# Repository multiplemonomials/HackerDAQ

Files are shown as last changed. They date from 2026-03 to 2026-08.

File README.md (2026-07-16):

# HackerDAQ: A Data Acquisition System for Hackers

HackerDAQ is a work-in-progress project to create an open-source data acquisition system. The project is currently in its early stages, but the goal is to create something that can be used in place of industrial DAQ systems to record high-quality data.

## Background and Motivation

The tech industry is in kind of a weird place when it comes to data acquisition (DAQ) systems. Suppose you have some sort of mechanical system you want to work with -- maybe a science experiment, maybe an industrial process, maybe an automation system, who knows. You have some sensors that you need to read and record the data from, and maybe you want to control some outputs as well, like turning the power on to some valves/solenoids/motors in response to a sensor reading. To do this, you need a DAQ system. However, an odd divide exists in the DAQ industry right now, between the incredibly professional and the almost insultingly hobbyist.

At one end of the spectrum, there are industrial-grade offerings from companies like National Instruments, Beckhoff, and Dewesoft. These systems are capable, flexible, and reliable -- but also extremely expensive. Even an entry-level NI system will run you well into the mid 4 figures, and other manufacturers are similar or worse. What if you can't afford that? Well, in many cases, your only option is getting an Arduino or Raspberry Pi and some basic dev boards for the sensors you need, and then hacking together enough software to log the data over serial. I've seen this many times, and while it does sometimes work, by doing it, you give up a lot of niceties like defined accuracy, noise resistance, a constant sample rate, etc.

Meanwhile, technology has moved on, and we're now in an era where highly accurate, multi-input Analog-Digital Converter (ADC) chips can be purchased very cheaply. This project has selected the [AD7770](https://www.analog.com/en/products/ad7770.html) from Analog Devices, a 21-bit, 32kHz, 8-input ADC which can be purchased for about $15 each at quantity. Using this chip enables DAQ devices to be made quite simply and cheaply, as one basically just needs to attach different front-ends to this chip to convert the signals based on the sensor being sampled. With the existence of this chip and others like it, there is really no justification for DAQ devices to cost thousands of dollars unless you need better accuracy or sampling rate than these types of ADCs can provide.

## Basic Overview

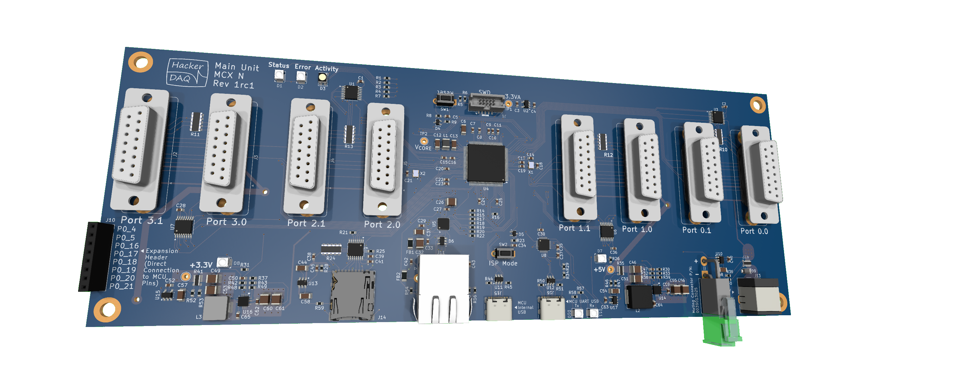
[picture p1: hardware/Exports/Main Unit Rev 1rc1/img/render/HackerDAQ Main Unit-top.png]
Main unit render


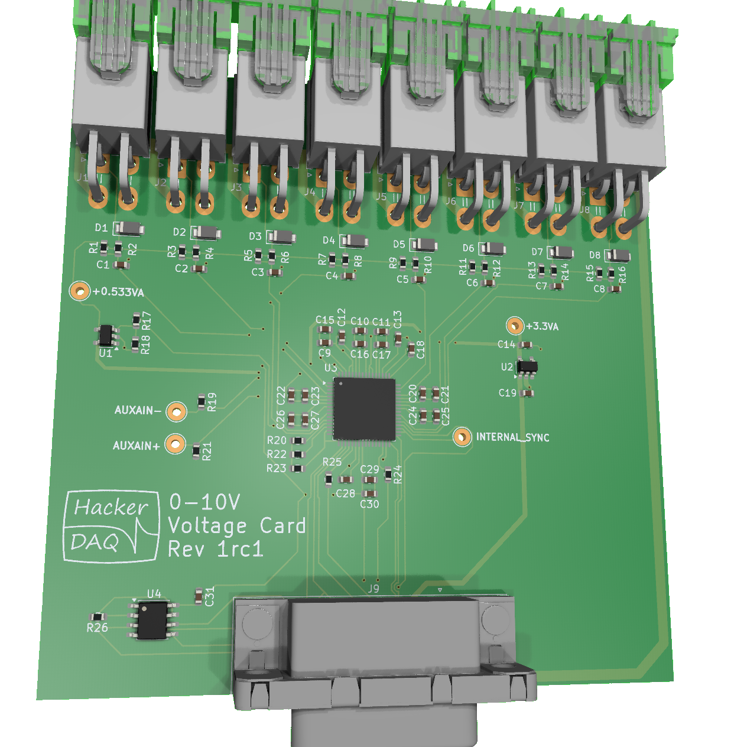
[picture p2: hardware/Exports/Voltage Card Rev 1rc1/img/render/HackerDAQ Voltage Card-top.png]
Voltage card render


The HackerDAQ consists of a main board with a microcontroller on it and basic circuitry such as power supplies, an Ethernet port, and a MicroSD slot. The main board would have a number of connectors for cards to plug in, each of which carries power, GPIOs, and SPI bus signals.

Cards can be designed for many different applications, including digital I/O and many different types of analog sensors. The user can select only the cards they need for the application they have in mind, keeping the base cost of the system down and allowing the user to get exactly the I/O they need. The SPI bus was selected for communications with these cards as it is fast, there are a wide range of chips available that speak it, and it supports bussing together multiple chips on the card over one set of bus lines. In a lot of ways, these cards are similar to existing sensor interconnect systems like SparkFun Qwiic / Adafruit Stemma / Digilent Pmod, where you can buy various task-specific modules and connect them to a motherboard. This would just be focused more on DAQ stuff and be more industrial-grade.

In terms of software, the HackerDAQ would include firmware that would run on the board and interface with all the cards, send data to connected user interface(s), and receive and execute commands. On the PC side, there would be a basic program that can display and record data. For users who don't want to program, they can see the live data in the GUI, record it to a file, and manually control outputs. For users who are a little more comfortable with programming, they could write scripts (likely python) that would run on the host machine and be able to control the DAQ. And for users who have embedded software experience, they could write their own code that extends or replaces the firmware on the actual DAQ!

## Key Decisions

| Area | Decision | Why |
|------------|-------------|--------------|
|Physical architecture | Main board + swappable cards | <ul><li>Avoids need to create multi-function inputs which would increase complexity</li><li>Makes system cheaper if you only need a few types of inputs</li><li>Avoids need to mess around with external amplifiers or other circuitry for sensors that need them -- they can be built directly into the card</li><li>Allows for much wider range of off-the-shelf supported functionality</li></ul>|
|CPU|NXP MCX Alpha Microcontroller running Mbed OS|<ul><li>Using a microcontroller, rather than a linux CPU + supporting circuitry, keeps the cost down</li><li>Using an RTOS rather than a full OS makes microsecond-level timestamping and SPI transaction scheduling possible</li><li>This MCU has two CPU cores at 150 MHz, plus a powerful DMA controller, a fast internal bus, and lots of SPI connectivity</li></ul>|
|SPI bus topology|2 card connectors per SPI bus, one leader card and one follower. All cards on a given bus must share the same polling rate.|<ul><li>MCU does not have enough pins for each of the 8 slots to have its own dedicated SPI bus, so there needs to be some way for cards to share a bus.</li><li>In most real systems, you generally have a lot of sensors at the same data rate, so I do not expect this to be too crippling of a limitation</li></ul>|
|Connection to host|Ethernet, potential upgrade later to add USB|<ul><li>Ethernet provides high quality electrical isolation and is highly noise-immune, so it's great for industrial applications</li><li>Ethernet peripherals in microcontrollers are well-optimized for high data rate applications</li><li>Allows the DAQ to connect to a larger network and interact with multiple machines, plus receive time via NTP</li></ul>|
|Local recording|MicroSD (SPI based)|<ul><li>Important to have a method of locally recording data for standalone applications</li><li>Mbed has a preexisting driver for MicroSD cards in SPI mode</li><li>SDIO mode is faster but driver support is less present (though not totally hopeless either)</li></ul>|
|Card identification|4kiB SPI EEPROM on the card (thinking M95320-RMN6)|<ul><li>Allows SW to largely autoconfigure itself based on the cards that are physically installed</li><li>Provides a convenient place to store calibration data!</li></ul>|
|Card to sensor connectors|Molex Mini-Fit|<ul><li>I have used these connectors in the past and they are really balanced all-around:<ul><li>Retention clip ensures they can't vibrate loose</li><li>Rated for ~8A continuous per pin</li><li>Good size: not so small that they are hard to work with, but not so big that they make your entire system bigger</li></ul></li><li>Big downside is that the crimp tool costs $400. Could mitigate by supplying one wire harness with each card that users can splice their own sensor wires to</li></ul>|
|Card to main board connector|15-pin, 2 row D-Sub (DA-15)|<ul><li>Very cheap</li><li>Screws provide relatively beefy mechanical retention</li><li>Not a size used in consumer hardware so unlikely to be plugged in to, say, a monitor accidentally</li><li>Still uses standard D-sub hardware so it should be possible to get premade cables, crimpers, etc without too much trouble</li></ul>|

## The Main Unit
The main unit contains a high performance MCX Alpha microcontroller with Ethernet, multiple SPI busses, a MicroSD slot, and a number of extra GPIO pins. 

### Data Recording
Both the Ethernet and the MicroSD card are available for recording data. The Ethernet is for livestreaming when you want to view, record, and process data on a PC, while the MicroSD card would be used for simple applications where you just want to record locally, and could also be configured as a backup so that data isn’t lost if the ethernet connection drops out.

### Power
The main unit takes in and regulates power for the HackerDAQ system. It has a DC input which can handle up to 8A at a variable voltage (9-24V). This voltage, referred to as Vsupply, is sent through the connectors into the cards for use as a higher voltage excitation supply when needed. High-current logic rails are provided for cards and attached devices to use -- currently 5V@8A and 3.3V@8A.

### Card Ports
The main unit has four SPI busses. Each SPI bus provides two card ports, a "leader" port and a "follower" port. The leader and follower ports on a given bus can have different cards connected, but *must* operate at the same speed as SPI transactions for all cards will happen at a fixed cycle rate for the bus.

### Expansion Port
Some of the microcontroller I/O pins that are not connected to one of the SPI busses are routed to the expansion port. This will include some digital pins (with I2C/PWM/UART) and some analog pins. Advanced users who are comfortable programming embedded C++ can add write their own software that uses these pins. This allows the HackerDAQ to be used as a jumping-off point for one's own projects!

Also, SWD debug pins and reset pin are broken out to an ARM SWD debug connector, for use with a debug tool like a J-Link or MCU-Link.

### Open Questions
- Is it worth adding a battery-backed RTC so that the time can be maintained if there is a power outage?
- Does PoE support make sense?

### Card Interface
The main unit would provide the following signals to each card:
- SPI signals (MOSI, MISO, SCLK)
- 3x CS lines
    - This allows having 2 addressable chips on the card side, plus the EEPROM
    - 8.192MHz clock signal for the ADC
    - +12V, +5V, and +3.3V digital rails
    - A data ready line from the card
    - A sync line to the card

### Analog Card Basics
Each analog card would contain the same basic DNA:
- Analog front-end, with ESD protection and passive filtering
- Instrumentation amplifier, if needed
- Voltage reference, LTC6658 on cards that need to supply precision excitation voltage, other cheaper option (or built-in ref) if only voltage input is needed
- Multi-input ADC with SPI interface
- SPI EEPROM that stores the card's identity information and calibration

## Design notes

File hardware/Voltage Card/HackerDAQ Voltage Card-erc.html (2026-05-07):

Logo

| ERC report for HackerDAQ Voltage Card
| Schematic: HackerDAQ Voltage Card Revision: Date: 2026-05-06T20:08:41-0700 KiCad Version: 9.0.7 | Errors: 0 Warnings: 58 Total: 58

Sheet / (HackerDAQ Voltage Card.kicad_sch)

Type | Description | Details
lib_symbol_mismatch | Symbol '+8V' doesn't match copy in library 'power' | @(0.1905 mm, 0.2413 mm): Symbol #PWR017 [+8V]
footprint_link_issues | Footprint 'Molex_Mini-Fit_Jr_5569-04A2_2x02_P4.20mm_Horizontal' not found in library 'Project Library'. | @(0.3048 mm, 0.3048 mm): Symbol J1 [MiniFit_Jr_5569_04A2]
lib_symbol_mismatch | Symbol '+8V' doesn't match copy in library 'power' | @(0.1905 mm, 0.4572 mm): Symbol #PWR018 [+8V]
lib_symbol_mismatch | Symbol 'GND' doesn't match copy in library 'power' | @(0.3937 mm, 0.3302 mm): Symbol #PWR015 [GND]
footprint_link_issues | Footprint 'Molex_Mini-Fit_Jr_5569-04A2_2x02_P4.20mm_Horizontal' not found in library 'Project Library'. | @(0.3048 mm, 0.5207 mm): Symbol J2 [MiniFit_Jr_5569_04A2]
lib_symbol_mismatch | Symbol 'GND' doesn't match copy in library 'power' | @(0.3937 mm, 0.5461 mm): Symbol #PWR019 [GND]
lib_symbol_mismatch | Symbol '+8V' doesn't match copy in library 'power' | @(0.1905 mm, 0.6731 mm): Symbol #PWR020 [+8V]
footprint_link_issues | Footprint 'Molex_Mini-Fit_Jr_5569-04A2_2x02_P4.20mm_Horizontal' not found in library 'Project Library'. | @(0.3048 mm, 0.7366 mm): Symbol J3 [MiniFit_Jr_5569_04A2]
lib_symbol_mismatch | Symbol 'GND' doesn't match copy in library 'power' | @(0.3937 mm, 0.762 mm): Symbol #PWR021 [GND]
lib_symbol_mismatch | Symbol '+8V' doesn't match copy in library 'power' | @(0.1905 mm, 0.889 mm): Symbol #PWR022 [+8V]
footprint_link_issues | Footprint 'Molex_Mini-Fit_Jr_5569-04A2_2x02_P4.20mm_Horizontal' not found in library 'Project Library'. | @(0.3048 mm, 0.9525 mm): Symbol J4 [MiniFit_Jr_5569_04A2]
lib_symbol_mismatch | Symbol 'GND' doesn't match copy in library 'power' | @(0.3937 mm, 0.9779 mm): Symbol #PWR023 [GND]
lib_symbol_mismatch | Symbol '+8V' doesn't match copy in library 'power' | @(0.1905 mm, 1.1049 mm): Symbol #PWR024 [+8V]
footprint_link_issues | Footprint 'Molex_Mini-Fit_Jr_5569-04A2_2x02_P4.20mm_Horizontal' not found in library 'Project Library'. | @(0.3048 mm, 1.1684 mm): Symbol J5 [MiniFit_Jr_5569_04A2]
lib_symbol_mismatch | Symbol 'GND' doesn't match copy in library 'power' | @(0.3937 mm, 1.1938 mm): Symbol #PWR025 [GND]
footprint_link_issues | Footprint 'NetTie-2_SMD_Pad0.2mm' not found in library 'Project Library'. | @(1.2446 mm, 0.3429 mm): Symbol NT1 [NetTie_2]
footprint_link_issues | Footprint 'NetTie-2_SMD_Pad0.2mm' not found in library 'Project Library'. | @(1.2446 mm, 0.3683 mm): Symbol NT2 [NetTie_2]
footprint_link_issues | Footprint 'NetTie-2_SMD_Pad0.2mm' not found in library 'Project Library'. | @(1.2446 mm, 0.3937 mm): Symbol NT3 [NetTie_2]
footprint_link_issues | Footprint 'NetTie-2_SMD_Pad0.2mm' not found in library 'Project Library'. | @(1.2446 mm, 0.4191 mm): Symbol NT4 [NetTie_2]
footprint_link_issues | Footprint 'NetTie-2_SMD_Pad0.2mm' not found in library 'Project Library'. | @(1.2446 mm, 0.4445 mm): Symbol NT5 [NetTie_2]
footprint_link_issues | Footprint 'NetTie-2_SMD_Pad0.2mm' not found in library 'Project Library'. | @(1.2446 mm, 0.4699 mm): Symbol NT6 [NetTie_2]
lib_symbol_mismatch | Symbol '+8V' doesn't match copy in library 'power' | @(0.1905 mm, 1.3208 mm): Symbol #PWR026 [+8V]
footprint_link_issues | Footprint 'NetTie-2_SMD_Pad0.2mm' not found in library 'Project Library'. | @(1.2446 mm, 0.4953 mm): Symbol NT7 [NetTie_2]
footprint_link_issues | Footprint 'NetTie-2_SMD_Pad0.2mm' not found in library 'Project Library'. | @(1.2446 mm, 0.5207 mm): Symbol NT8 [NetTie_2]
lib_symbol_mismatch | Symbol 'HT' doesn't match copy in library 'power' | @(1.2319 mm, 0.6223 mm): Symbol #PWR038 [HT]
footprint_link_issues | Footprint 'Molex_Mini-Fit_Jr_5569-04A2_2x02_P4.20mm_Horizontal' not found in library 'Project Library'. | @(0.3048 mm, 1.3843 mm): Symbol J6 [MiniFit_Jr_5569_04A2]
lib_symbol_mismatch | Symbol 'GND' doesn't match copy in library 'power' | @(0.3937 mm, 1.4097 mm): Symbol #PWR027 [GND]
lib_symbol_mismatch | Symbol '+8V' doesn't match copy in library 'power' | @(0.1905 mm, 1.5367 mm): Symbol #PWR028 [+8V]
footprint_link_issues | Footprint 'Molex_Mini-Fit_Jr_5569-04A2_2x02_P4.20mm_Horizontal' not found in library 'Project Library'. | @(0.3048 mm, 1.6002 mm): Symbol J7 [MiniFit_Jr_5569_04A2]
lib_symbol_mismatch | Symbol '+8V' doesn't match copy in library 'power' | @(1.3335 mm, 1.0033 mm): Symbol #PWR048 [+8V]
lib_symbol_mismatch | Symbol 'GND' doesn't match copy in library 'power' | @(0.3937 mm, 1.6256 mm): Symbol #PWR031 [GND]
lib_symbol_mismatch | Symbol '+8V' doesn't match copy in library 'power' | @(0.1905 mm, 1.778 mm): Symbol #PWR030 [+8V]
lib_symbol_mismatch | Symbol '-5V' doesn't match copy in library 'power' | @(1.8034 mm, 0.1651 mm): Symbol #PWR016 [-5V]
footprint_link_issues | Footprint 'Molex_Mini-Fit_Jr_5569-04A2_2x02_P4.20mm_Horizontal' not found in library 'Project Library'. | @(0.3048 mm, 1.8415 mm): Symbol J8 [MiniFit_Jr_5569_04A2]
lib_symbol_mismatch | Symbol 'GND' doesn't match copy in library 'power' | @(0.3937 mm, 1.8669 mm): Symbol #PWR029 [GND]
lib_symbol_mismatch | Symbol 'GND' doesn't match copy in library 'power' | @(1.8161 mm, 0.5969 mm): Symbol #PWR014 [GND]
lib_symbol_mismatch | Symbol '+8V' doesn't match copy in library 'power' | @(1.905 mm, 0.1651 mm): Symbol #PWR037 [+8V]
lib_symbol_mismatch | Symbol '-5V' doesn't match copy in library 'power' | @(1.3716 mm, 1.397 mm): Symbol #PWR011 [-5V]
lib_symbol_issues | Symbol 'OPA310xDBV' not found in symbol library 'Amplifier_Operational' | @(1.3462 mm, 1.4986 mm): Symbol U2 [OPA310xDBV]
lib_symbol_mismatch | Symbol 'HT' doesn't match copy in library 'power' | @(1.524 mm, 1.3843 mm): Symbol #PWR010 [HT]
lib_symbol_mismatch | Symbol 'GND' doesn't match copy in library 'power' | @(1.3716 mm, 1.6002 mm): Symbol #PWR08 [GND]
lib_symbol_mismatch | Symbol 'GND' doesn't match copy in library 'power' | @(1.524 mm, 1.5621 mm): Symbol #PWR09 [GND]
footprint_link_issues | Footprint 'HackerDAQ Logo' not found in library 'Project Library'. | @(1.8415 mm, 1.7018 mm): Symbol LG1 [HackerDAQ_Logo]
lib_symbol_mismatch | Symbol '-5V' doesn't match copy in library 'power' | @(2.1336 mm, 1.397 mm): Symbol #PWR012 [-5V]
lib_symbol_mismatch | Symbol '+8V' doesn't match copy in library 'power' | @(2.5527 mm, 0.508 mm): Symbol #PWR034 [+8V]
lib_symbol_mismatch | Symbol '+8V' doesn't match copy in library 'power' | @(2.5908 mm, 0.5461 mm): Symbol #PWR035 [+8V]
lib_symbol_mismatch | Symbol '+8V' doesn't match copy in library 'power' | @(2.6289 mm, 0.5842 mm): Symbol #PWR036 [+8V]
lib_symbol_mismatch | Symbol 'GND' doesn't match copy in library 'power' | @(2.286 mm, 1.5748 mm): Symbol #PWR013 [GND]
lib_symbol_mismatch | Symbol 'GND' doesn't match copy in library 'power' | @(2.6924 mm, 0.8763 mm): Symbol #PWR039 [GND]
lib_symbol_mismatch | Symbol '+8V' doesn't match copy in library 'power' | @(2.54 mm, 1.397 mm): Symbol #PWR032 [+8V]
lib_symbol_mismatch | Symbol 'GND' doesn't match copy in library 'power' | @(0.6858 mm, 0.5334 mm): Symbol #PWR047 [GND]
lib_symbol_mismatch | Symbol 'GND' doesn't match copy in library 'power' | @(1.1303 mm, 0.635 mm): Symbol #PWR07 [GND]
footprint_link_issues | Footprint 'LFCSP-64-1EP_9x9mm_P0.5mm_EP5.21x5.21mm_LeadsExtended' not found in library 'Project Library'. | @(2.0955 mm, 1.4224 mm): Symbol U1 [AD7770]
lib_symbol_mismatch | Symbol 'GND' doesn't match copy in library 'power' | @(0.8382 mm, 0.6477 mm): Symbol #PWR049 [GND]
lib_symbol_mismatch | Symbol 'GND' doesn't match copy in library 'power' | @(0.9398 mm, 0.8636 mm): Symbol #PWR050 [GND]
footprint_link_issues | Footprint 'Amphenol_LD15S33E4GX00LF' not found in library 'Project Library'. | @(1.27 mm, 0.5969 mm): Symbol J9 [DA15_Socket_MountingHoles]
lib_symbol_issues | Symbol 'DA15_Socket_MountingHoles' not found in symbol library 'Connector' | @(1.27 mm, 0.5969 mm): Symbol J9 [DA15_Socket_MountingHoles]
lib_symbol_mismatch | Symbol 'GND' doesn't match copy in library 'power' | @(1.27 mm, 0.8636 mm): Symbol #PWR033 [GND]

Generated by KiBot (https://github.com/INTI-CMNB/KiBot/) v1.8.5

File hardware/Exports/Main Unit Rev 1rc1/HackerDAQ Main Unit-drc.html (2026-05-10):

Logo

| DRC report for HackerDAQ Main Unit
| PCB: HackerDAQ Main Unit Revision: Date: 2026-05-10T05:28:41+0000 KiCad Version: 9.0.7 | Errors: 0 Warnings: 0 Total: 0

✔

Generated by KiBot (https://github.com/INTI-CMNB/KiBot/) v1.8.5

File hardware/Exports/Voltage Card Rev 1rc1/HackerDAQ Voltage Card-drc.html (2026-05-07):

Logo

| DRC report for HackerDAQ Voltage Card
| PCB: HackerDAQ Voltage Card Revision: Date: 2026-05-07T05:04:43+0000 KiCad Version: 9.0.7 | Errors: 0 Warnings: 60 (+1 excluded) Total: 60 (+1 excluded)

Violations

Type | Description | Details
lib_footprint_mismatch | Footprint 'C_0603_1608Metric' does not match copy in library 'Capacitor_SMD'. | @(102.25 mm, 97.975 mm): Footprint C20
lib_footprint_mismatch | Footprint 'R_0603_1608Metric' does not match copy in library 'Resistor_SMD'. | @(99.354081 mm, 78.0 mm): Footprint R9
lib_footprint_mismatch | Footprint 'R_0603_1608Metric' does not match copy in library 'Resistor_SMD'. | @(57.5 mm, 78.0 mm): Footprint R2
lib_footprint_mismatch | Footprint 'C_0603_1608Metric' does not match copy in library 'Capacitor_SMD'. | @(69.009259 mm, 80.5 mm): Footprint C2
lib_footprint_mismatch | Footprint 'C_0603_1608Metric' does not match copy in library 'Capacitor_SMD'. | @(58.0 mm, 80.5 mm): Footprint C1
lib_footprint_mismatch | Footprint 'R_0603_1608Metric' does not match copy in library 'Resistor_SMD'. | @(112.285271 mm, 78.0 mm): Footprint R12
lib_footprint_mismatch | Footprint 'R_0603_1608Metric' does not match copy in library 'Resistor_SMD'. | @(88.3 mm, 110.8 mm): Footprint R25
lib_footprint_mismatch | Footprint 'C_0603_1608Metric' does not match copy in library 'Capacitor_SMD'. | @(87.575 mm, 90.8 mm): Footprint C15
lib_footprint_mismatch | Footprint 'C_0603_1608Metric' does not match copy in library 'Capacitor_SMD'. | @(70.5 mm, 126.99 mm): Footprint C31
lib_footprint_mismatch | Footprint 'C_0603_1608Metric' does not match copy in library 'Capacitor_SMD'. | @(92.8 mm, 88.8 mm): Footprint C10
lib_footprint_mismatch | Footprint 'C_0603_1608Metric' does not match copy in library 'Capacitor_SMD'. | @(104.25 mm, 97.975 mm): Footprint C21
lib_footprint_mismatch | Footprint 'C_0603_1608Metric' does not match copy in library 'Capacitor_SMD'. | @(84.8 mm, 102.3 mm): Footprint C27
lib_footprint_mismatch | Footprint 'C_0603_1608Metric' does not match copy in library 'Capacitor_SMD'. | @(101.854081 mm, 80.5 mm): Footprint C5
lib_footprint_mismatch | Footprint 'C_0603_1608Metric' does not match copy in library 'Capacitor_SMD'. | @(118.5 mm, 90.0 mm): Footprint C14
lib_footprint_mismatch | Footprint 'C_0603_1608Metric' does not match copy in library 'Capacitor_SMD'. | @(102.3 mm, 101.3 mm): Footprint C24
lib_footprint_mismatch | Footprint 'R_0603_1608Metric' does not match copy in library 'Resistor_SMD'. | @(88.55191 mm, 78.0 mm): Footprint R7
lib_footprint_mismatch | Footprint 'R_0603_1608Metric' does not match copy in library 'Resistor_SMD'. | @(83.8 mm, 109.3 mm): Footprint R23
lib_footprint_mismatch | Footprint 'C_0603_1608Metric' does not match copy in library 'Capacitor_SMD'. | @(100.575 mm, 91.3 mm): Footprint C18
lib_footprint_mismatch | Footprint 'C_0603_1608Metric' does not match copy in library 'Capacitor_SMD'. | @(90.075 mm, 89.8 mm): Footprint C12
lib_footprint_mismatch | Footprint 'R_0603_1608Metric' does not match copy in library 'Resistor_SMD'. | @(83.8 mm, 107.3 mm): Footprint R22
lib_footprint_mismatch | Footprint 'R_0603_1608Metric' does not match copy in library 'Resistor_SMD'. | @(97.0 mm, 110.0 mm): Footprint R24
lib_footprint_mismatch | Footprint 'C_0603_1608Metric' does not match copy in library 'Capacitor_SMD'. | @(133.5 mm, 80.5 mm): Footprint C8
lib_footprint_mismatch | Footprint 'R_0603_1608Metric' does not match copy in library 'Resistor_SMD'. | @(101.354081 mm, 78.0 mm): Footprint R10
lib_footprint_mismatch | Footprint 'R_0603_1608Metric' does not match copy in library 'Resistor_SMD'. | @(77.548571 mm, 78.0 mm): Footprint R5
lib_footprint_mismatch | Footprint 'R_0603_1608Metric' does not match copy in library 'Resistor_SMD'. | @(121.437784 mm, 78.0 mm): Footprint R13
lib_footprint_mismatch | Footprint 'C_0603_1608Metric' does not match copy in library 'Capacitor_SMD'. | @(94.3 mm, 110.8 mm): Footprint C29
lib_footprint_mismatch | Footprint 'C_0603_1608Metric' does not match copy in library 'Capacitor_SMD'. | @(112.785271 mm, 80.5 mm): Footprint C6
lib_footprint_mismatch | Footprint 'R_0603_1608Metric' does not match copy in library 'Resistor_SMD'. | @(90.55191 mm, 78.0 mm): Footprint R8
lib_footprint_mismatch | Footprint 'C_0603_1608Metric' does not match copy in library 'Capacitor_SMD'. | @(91.05191 mm, 80.5 mm): Footprint C4
lib_footprint_mismatch | Footprint 'R_0603_1608Metric' does not match copy in library 'Resistor_SMD'. | @(69.5 mm, 107.0 mm): Footprint R21
lib_footprint_mismatch | Footprint 'R_0603_1608Metric' does not match copy in library 'Resistor_SMD'. | @(60.5 mm, 88.5 mm): Footprint R17
lib_footprint_mismatch | Footprint 'C_0603_1608Metric' does not match copy in library 'Capacitor_SMD'. | @(118.5 mm, 97.5 mm): Footprint C19
lib_footprint_mismatch | Footprint 'C_0603_1608Metric' does not match copy in library 'Capacitor_SMD'. | @(98.575 mm, 89.8 mm): Footprint C13
lib_footprint_mismatch | Footprint 'R_0603_1608Metric' does not match copy in library 'Resistor_SMD'. | @(110.285271 mm, 78.0 mm): Footprint R11
lib_footprint_mismatch | Footprint 'R_0603_1608Metric' does not match copy in library 'Resistor_SMD'. | @(123.437784 mm, 78.0 mm): Footprint R14
lib_footprint_mismatch | Footprint 'C_0603_1608Metric' does not match copy in library 'Capacitor_SMD'. | @(123.937784 mm, 80.5 mm): Footprint C7
lib_footprint_mismatch | Footprint 'R_0603_1608Metric' does not match copy in library 'Resistor_SMD'. | @(66.509259 mm, 78.0 mm): Footprint R3
lib_footprint_mismatch | Footprint 'R_0603_1608Metric' does not match copy in library 'Resistor_SMD'. | @(79.548571 mm, 78.0 mm): Footprint R6
lib_footprint_mismatch | Footprint 'R_0603_1608Metric' does not match copy in library 'Resistor_SMD'. | @(68.509259 mm, 78.0 mm): Footprint R4
lib_footprint_mismatch | Footprint 'C_0603_1608Metric' does not match copy in library 'Capacitor_SMD'. | @(94.3 mm, 112.8 mm): Footprint C30
lib_footprint_mismatch | Footprint 'C_0603_1608Metric' does not match copy in library 'Capacitor_SMD'. | @(82.8 mm, 102.3 mm): Footprint C26
lib_footprint_mismatch | Footprint 'R_0603_1608Metric' does not match copy in library 'Resistor_SMD'. | @(133.0 mm, 78.0 mm): Footprint R16
lib_footprint_mismatch | Footprint 'SOIC-8_3.9x4.9mm_P1.27mm' does not match copy in library 'Package_SO'. | @(64.5 mm, 130.0 mm): Footprint U4
lib_footprint_mismatch | Footprint 'R_0603_1608Metric' does not match copy in library 'Resistor_SMD'. | @(57.25 mm, 129.5 mm): Footprint R26
lib_footprint_mismatch | Footprint 'C_0603_1608Metric' does not match copy in library 'Capacitor_SMD'. | @(82.75 mm, 98.75 mm): Footprint C22
lib_footprint_mismatch | Footprint 'SOT-23-5' does not match copy in library 'Package_TO_SOT_SMD'. | @(118.5 mm, 93.5 mm): Footprint U2
lib_footprint_mismatch | Footprint 'C_0603_1608Metric' does not match copy in library 'Capacitor_SMD'. | @(104.3 mm, 101.3 mm): Footprint C25
lib_footprint_mismatch | Footprint 'C_0603_1608Metric' does not match copy in library 'Capacitor_SMD'. | @(90.8 mm, 110.8 mm): Footprint C28
lib_footprint_mismatch | Footprint 'R_0603_1608Metric' does not match copy in library 'Resistor_SMD'. | @(131.0 mm, 78.0 mm): Footprint R15
lib_footprint_mismatch | Footprint 'R_0603_1608Metric' does not match copy in library 'Resistor_SMD'. | @(60.5 mm, 92.0 mm): Footprint R18
lib_footprint_mismatch | Footprint 'C_0603_1608Metric' does not match copy in library 'Capacitor_SMD'. | @(87.575 mm, 88.8 mm): Footprint C9
lib_footprint_mismatch | Footprint 'C_0603_1608Metric' does not match copy in library 'Capacitor_SMD'. | @(84.75 mm, 98.75 mm): Footprint C23
lib_footprint_mismatch | Footprint 'R_0603_1608Metric' does not match copy in library 'Resistor_SMD'. | @(83.8 mm, 105.3 mm): Footprint R20
lib_footprint_mismatch | Footprint 'R_0603_1608Metric' does not match copy in library 'Resistor_SMD'. | @(55.5 mm, 78.0 mm): Footprint R1
lib_footprint_mismatch | Footprint 'C_0603_1608Metric' does not match copy in library 'Capacitor_SMD'. | @(96.075 mm, 90.8 mm): Footprint C17
lib_footprint_mismatch | Footprint 'C_0603_1608Metric' does not match copy in library 'Capacitor_SMD'. | @(92.8 mm, 90.8 mm): Footprint C16
lib_footprint_mismatch | Footprint 'SOT-23-5' does not match copy in library 'Package_TO_SOT_SMD'. | @(56.5 mm, 91.0 mm): Footprint U1
lib_footprint_mismatch | Footprint 'C_0603_1608Metric' does not match copy in library 'Capacitor_SMD'. | @(96.075 mm, 88.8 mm): Footprint C11
lib_footprint_mismatch | Footprint 'R_0603_1608Metric' does not match copy in library 'Resistor_SMD'. | @(70.0 mm, 100.0 mm): Footprint R19
lib_footprint_mismatch | Footprint 'C_0603_1608Metric' does not match copy in library 'Capacitor_SMD'. | @(80.048571 mm, 80.5 mm): Footprint C3
silk_edge_clearance | Silkscreen clipped by board edge | @(50.0 mm, 50.0 mm): Rectangle on Edge.Cuts @(114.555 mm, 127.159669 mm): Segment of J9 on F.Silkscreen

Generated by KiBot (https://github.com/INTI-CMNB/KiBot/) v1.8.5

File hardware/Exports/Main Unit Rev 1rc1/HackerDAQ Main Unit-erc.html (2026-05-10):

Logo

| ERC report for HackerDAQ Main Unit
| Schematic: HackerDAQ Main Unit Revision: Date: 2026-05-10T05:28:37+0000 KiCad Version: 9.0.7 | Errors: 0 Warnings: 0 Total: 0

✔

Generated by KiBot (https://github.com/INTI-CMNB/KiBot/) v1.8.5

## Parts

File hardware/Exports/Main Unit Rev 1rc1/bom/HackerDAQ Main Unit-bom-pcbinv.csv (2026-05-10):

References | Description | Part | Value | Supplier | SKU | Footprint | LibRef | Qty
C47 C50 | Unpolarized capacitor, small symbol | C_Small | 150pF | Digi-Key | 478-KGM15ACG2A151FTCT-ND | C_0603_1608Metric | KGM15ACG2A151FT | 2
C1 C2 C4 C5 C7 C8 C10 C15 C16 C17 C18 C19 C20 C21 C22 C24 C25 C27 C28 C29 C30 C33 C34 C35 C36 C38 C40 C42 C43 C52 C59 C62 C63 C64 C65 | Unpolarized capacitor, small symbol | C_Small | 100nF | Digi-Key | 399-C0603C104K5RACTUCT-ND | C_0603_1608Metric | ESD35C104K4T2A-24 | 35
C11 | Unpolarized capacitor, small symbol | C_Small | 220nF | Digi-Key | 490-4935-1-ND | C_0603_1608Metric | GCM188R71E224KA55D | 1
C3 C9 C14 C23 C37 C39 C41 C45 | Unpolarized capacitor, small symbol | C_Small | 1µF | Digi-Key | 1276-6524-1-ND | C_0603_1608Metric | CL10B105MO8NNWC | 8
C6 C31 | Unpolarized capacitor, small symbol | C_Small | 2.2µF | Digi-Key | 1276-3137-1-ND | C_1206_3216Metric | CL31B225KBHNNNE | 2
C12 C13 C44 C48 C54 C57 C58 | Unpolarized capacitor, small symbol | C_Small | 10µF | Digi-Key |  | C_1206_3216Metric | CL31B106KLHNNNE | 7
C55 C56 C60 C61 | Unpolarized capacitor, small symbol | C_Small | 10µF | Digi-Key | 1276-3387-1-ND | C_1210_3225Metric | CL32B106KBJNNNE | 4
C26 C32 C46 C49 C51 C53 | Unpolarized capacitor, small symbol | C_Small | 22µF | Digi-Key | 1276-3395-1-ND | C_1210_3225Metric | CL32B226MOJNNNE | 6
D7 D8 | Green LED 100mcd 20mA Vf=2.1V | AA3528CGSK | AA3528CGSK |  | 754-1528-1-ND | AA3528 |  | 2
D1 D10 | Blue LED 150mcd 20mA Vf=3.3V | AA3528QBS | AA3528QBS |  | 754-1533-1-ND | AA3528 |  | 2
D2 | Red LED 100mcd 20mA Vf=1.95V | AA3528SURSK | AA3528SURSK |  | 754-1537-1-ND | AA3528 |  | 1
D11 | Yellow LED 200mcd 20mA Vf=2V | AA3528SYSK | AA3528SYSK |  | 754-1539-1-ND | AA3528 |  | 1
D3 | Tricolor Black Surface LED, 20mA, Common Anode Pin 1, PLCC-4 | ASMB-MTB0-0A3A2 | ASMB-MTB0-0B3A2 | Digi-Key | 516-ASMB-MTB0-0B3A2CT-ND | LED_Avago_PLCC4_3.2x2.8mm_CW_Fixed3DModel |  | 1
D4 D5 | Schottky barrier diode, SOT-323 | BAT54W | BAT54W | Digi-Key | 4878-BAT54WCT-ND | SOT-323_SC-70 |  | 2
D6 | 4-channel 1Gbps TVS Diode Array, 2.3pF, 4.5V breakdown, 30kV contact & air gap, SOT-23-5 | ESDS304 | ESDS304 | Digi-Key | 296-ESDS304DBVRCT-ND | SOT-23-5 |  | 1
D9 | 200W unidirectional Transil Transient Voltage Suppressor, 11Vrwm, SMF | SMF11A | SMF24A | Digi-Key | F5823CT-ND | D_SMF |  | 1
FB1 FB2 | Ferrite bead, small symbol | FerriteBead_Small | 300@100MHz | Digi-Key | 732-4654-1-ND | R_1206_3216Metric | 742792121 | 2
J12 | Mini-Fit 2x1 Jack, Right-Angle | MiniFit_Jr_5569_01A2 | 0039300020 | Digi-Key | WM21351-ND | Molex_Mini-Fit_Jr_5569-02A2_2x01_P4.20mm_Horizontal |  | 1
J10 | Generic connector, single row, 01x08, script generated (kicad-library-utils/schlib/autogen/connector/) | Conn_01x08 | 1x8 | Digi-Key | SAM8866-ND | PinSocket_1x08_P2.54mm_Vertical | HEADER_8x1_LONG_TAIL | 1
J1 | 10 Pin 0.05" Pitch IDC Ribbon Cable Connector w/ Keying Shroud | 3221-10-0300-00 | 3221-10-0300-00 | Digi-Key |  | 3221-10-0300-00 |  | 1
J2 J3 J4 J5 J6 J7 J8 J9 | 15-pin D-SUB connector, socket (female) (low-density/2 columns), Mounting Hole | DA15_Socket_MountingHoles | 61801525123 | Digi-Key | 732-61801525123-ND | Wurth_61801525123 |  | 8
J14 | Micro SD Card Socket with card detection pins | Micro_SD_Card_Det_Hirose_DM3AT | DM3AT | Digi-Key | HR1964CT-ND | microSD_HC_Hirose_DM3AT-SF-PEJM5 |  | 1
J11 | Halo HFJ11, 10/100 Base-TX, two LEDs, RJ45, Shielded | RJ45_Halo_HFJ11-x2450E-LxxRL | HFJ11-2450E-L21RL | Digi-Key | 5843-HFJ11-2450E-L21RL-ND | RJ45_HALO_HFJ11-x2450E-LxxRL_Horizontal-Fixed3DModel |  | 1
J13 | DC Barrel Jack with a mounting pin | Barrel_Jack_MountingPin | PJ-063AH | Digi-Key | CP-063AH-ND | BarrelJack_CUI_PJ-063AH_Horizontal |  | 1
J15 J16 | USB 2.0-only 16P Type-C Receptacle connector | USB_C_Receptacle_USB2.0_16P | USB4105-GF-A | Digi-Key | 2073-USB4105-GF-ACT-ND | USB_C_Receptacle_GCT_USB4105-xx-A_16P_TopMnt_Horizontal-ExtraHoleClearance |  | 2
L1 | Inductor | L | 1.5µH | Digi-Key | 495-2640-1-ND | L_1210_3225Metric | B82422H1152K000 | 1
L3 | Inductor | L | 2.2μH | Digi-Key | 308-2464-1-ND | 0630CDMCDDS | 0630CDMCCDS-2R2MC | 1
L2 | Inductor | L | 3.3μH | Digi-Key | 541-1352-1-ND | L_Vishay_IHLP-3232 | IHLP3232DZER3R3M11 | 1
R27 R35 R41 | Shunt resistor with Kelvin connections, US symbol | R_Shunt_US | .0025 | Digi-Key | 4463-D1FCP0612D2M50FF-T5CT-ND | D1FCP0612 | D1FCP0612D2M50FF-T5 | 3
R36 R40 R46 R47 R52 R53 | Resistor, small US symbol | R_Small_US | 10 | Digi-Key | 311-10.0HRCT-ND | R_0603_1608Metric | RC0603FR-0710RL | 6
R1 R4 R7 R58 | Resistor, small US symbol | R_Small_US | 30 | Digi-Key | 311-30.0HRCT-ND | R_0603_1608Metric | RC0603FR-0730RL | 4
R15 R17 R19 R20 R21 | Resistor, small US symbol | R_Small_US | 33 | Digi-Key | P33.0HCT-ND | R_0603_1608Metric |  | 5
R2 R3 R31 R57 | Resistor, small US symbol | R_Small_US | 140 | Digi-Key | 311-140HRCT-ND | R_0603_1608Metric | RC0603FR-07140RL | 4
R26 R54 R55 | Resistor, small US symbol | R_Small_US | 270 | Digi-Key | 311-270HRCT-ND | R_0603_1608Metric | RC0603FR-07270RL | 3
R59 | Resistor, small US symbol | R_Small_US | 1k | Digi-Key | 311-1.00KHRCT-ND | R_0603_1608Metric | RC0603FR-071KL | 1
R9 R16 | Resistor, small US symbol | R_Small_US | 2.2k | Digi-Key | 311-2.20KHRCT-ND | R_0603_1608Metric |  | 2
R39 R49 | Resistor, small US symbol | R_Small_US | 3.01k | Digi-Key | 311-3.01KHRCT-ND | R_0603_1608Metric | RC0603FR-073K01L | 2
R34 R56 | Resistor, small US symbol | R_Small_US | 4.7k | Digi-Key | 311-4.70KHRCT-ND | R_0603_1608Metric | RC0603FR-074K7L | 2
R44 R45 R50 R51 | Resistor, small US symbol | R_Small_US | 5.1k | Digi-Key | 311-5.10KHRCT-ND | R_0603_1608Metric | RC0603FR-075K1L | 4
R22 | Resistor, small US symbol | R_Small_US | 6.49k | Digi-Key | 311-6.49KHRCT-ND | R_0603_1608Metric | RC0603FR-076K49L | 1
R10 R11 R12 R13 R24 | CTS 745C101 8 resistor network, star topology, bussed resistors, small US symbol | CTS 745C101 | 10k | DigiKey | 60-745C101103JPCT-ND | CTS 745C101 | 745C101103JP | 5
R5 R6 R8 R14 R18 R23 R25 R28 R29 R38 R48 | Resistor, small US symbol | R_Small_US | 10k | Digi-Key | 311-10.0KHRCT-ND | R_0603_1608Metric | RC0603FR-0710KL | 11
R33 R43 | Resistor, small US symbol | R_Small_US | 18.2k | Digi-Key | 311-18.2KHRCT-ND | R_0603_1608Metric | RC0603FR-0718K2L | 2
R42 | Resistor, small US symbol | R_Small_US | 45.3k | Digi-Key | 541-5433-1-ND | R_0603_1608Metric | CRCW060345K3FKEAC | 1
R30 R37 | Resistor, small US symbol | R_Small_US | 52.3k | Digi-Key | 311-52.3KHRCT-ND | R_0603_1608Metric | RC0603FR-0752K3L | 2
R32 | Resistor, small US symbol | R_Small_US | 73.2k | Digi-Key | 2019-RK73H1JTTD7322FCT-ND | R_0603_1608Metric | RK73H1JTTD7322F | 1
SW1 SW2 | Push button switch, generic, two pins | SW_Push | MJTP1243 | Digi-Key | 679-2452-ND | SW_PUSH_1P1T_6x3.5mm_H4.3_APEM_MJTP1243 |  | 2
U13 | Load Switch w/ Discharge Resistor | AP22913W6-7 | AP22913W6-7 | Digi-Key | AP22913W6-7DICT-ND | SOT-23-6 |  | 1
U8 | Full Speed USB to U(S)ART Bridge, 3MHz Max Speed, With GPIOs, 24-QFN | CY7C65223 | CY7C65223 | Digi-Key | 448-CY7C65223-24LTXI-ND | QFN-24-1EP_4x4mm_P0.5mm_EP2.65x2.65mm-LengthenedPads |  | 1
U10 U15 U17 | Current Sense Amplifier, 1 Circuit, Rail-to-Rail, 26V, Gain 100 V/V, SOT-23-5 | INA180A3 | INA180A3 | Digi-Key | 296-47654-1-ND | SOT-23-5 |  | 3
U5 | 10BASE-T/100BASE-TX PHY with RMII Support, 50 MHz input clock, QFN-24 | KSZ8081RND | KSZ8081RND | Digi-Key | 576-4177-1-ND | QFN-24-1EP_4x4mm_P0.5mm_EP2.6x2.6mm |  | 1
U4 | MCU ARM Cortex-M33 Dual Core, 150MHz, 512kiB RAM, 2MiB Flash | MCXN547VKLT | MCXN547VKLT |  |  | LQFP-100-1EP_14x14mm_P0.5mm_EP6.9x6.9mm_Fixed3DModel |  | 1
U9 | 4 Channel Bidirectional Level Shifter with Selectable Direction, TSSOP-16 | SN74AXC4T774 | SN74AXC4T774 | Digi-Key | 296-SN74AXC4T774PWRCT-ND | TSSOP-16_4.4x5mm_P0.65mm |  | 1
U1 U3 U6 U7 | CMOS QPDT analog multiplexer/demultiplexer, TSSOP-16 | SN74CB3Q3257PWR | SN74CB3Q3257PWR | Digi-Key | 296-19138-1-ND | TSSOP-16_4.4x5mm_P0.65mm |  | 4
U2 | 150mA Low Dropout Voltage Regulator, Fixed Output 3.3V, SOT-23-5 | TLV71333PDBV | TLV71333PDBV | Digi-Key | 296-35591-1-ND | SOT-23-5 |  | 1
U14 U16 | Buck Regulator 10A 4.5-28V Input 0.6-13V Output QFN | TPS56A37RPAR | TPS56A37RPAR | Digi-Key | 296-TPS56A37RPARCT-ND | RPA0010A-MFG |  | 2
U11 U12 | Very low capacitance ESD protection diode, 2 data-line, SOT-23-6 | USBLC6-2SC6 | USBLC6-2SC6 | Digi-Key | 497-5235-1-ND | SOT-23-6 |  | 2
X1 | HCMOS Crystal Clock Oscillator, 2.5x2.0 mm SMD | ECS-2520MV-xxx-xx | 24.0000MHz | Digi-Key | XC2257CT-ND | Oscillator_SMD_ECS_2520MV-xxx-xx-4Pin_2.5x2.0mm_Fixed3DModel | ECS-TXO-2520-33-240-AN-TR | 1
X2 | HCMOS Crystal Clock Oscillator, 2.5x2.0 mm SMD | ECS-2520MV-xxx-xx | 8.192MHz | Digi-Key | 50-ECS-2520MVLC-081.92-BN-CT-ND | Oscillator_SMD_ECS_2520MV-xxx-xx-4Pin_2.5x2.0mm_Fixed3DModel | ECS-2520MVLC-081.92-BN | 1

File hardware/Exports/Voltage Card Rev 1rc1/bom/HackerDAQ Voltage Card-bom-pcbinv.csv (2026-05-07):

References | Description | Part | Value | Supplier | SKU | Footprint | LibRef | Qty
C1 C2 C3 C4 C5 C6 C7 C8 | Unpolarized capacitor, small symbol | C_Small | 1nF | Digi-Key | 490-1451-1-ND | C_0603_1608Metric | CL10B102KC8WPNC | 8
C10 C15 C17 C18 C19 C20 C23 C24 C27 C29 C31 | Unpolarized capacitor, small symbol | C_Small | 100nF | Digi-Key | 399-C0603C104K5RACTUCT-ND | C_0603_1608Metric | ESD35C104K4T2A-24 | 11
C9 C11 C12 C13 C14 C16 C21 C22 C25 C26 C28 C30 | Unpolarized capacitor, small symbol | C_Small | 1µF | Digi-Key | 1276-6524-1-ND | C_0603_1608Metric | CL10B105MO8NNWC | 12
D1 D2 D3 D4 D5 D6 D7 D8 | 200W unidirectional Transil Transient Voltage Suppressor, 11Vrwm, SMF | SMF11A | SMF11A | Digi-Key | F5746CT-ND | D_SMF |  | 8
J1 J2 J3 J4 J5 J6 J7 J8 | Mini-Fit 2x2 Jack, Right-Angle | MiniFit_Jr_5569_04A2 | 0039301040 | Digi-Key | WM1352-ND | Molex_Mini-Fit_Jr_5569-04A2_2x02_P4.20mm_Horizontal |  | 8
J9 | 15-pin D-SUB connector, socket (female) (low-density/2 columns), Mounting Hole | DA15_Socket_MountingHoles | LD15S33E4GX00LF | Digi-Key | LD15S33E4GX00LF-ND | Amphenol_LD15S33E4GX00LF |  | 1
R24 R25 R26 | Resistor, small US symbol | R_Small_US | 33 | Digi-Key | P33.0HCT-ND | R_0603_1608Metric | ERJ-3EKF33R0V | 3
R1 R3 R5 R7 R9 R11 R13 R15 | Resistor, small US symbol | R_Small_US | 3.4k | Digi-Key | YAG1653CT-ND | R_0603_1608Metric | RT0603BRD073K4L | 8
R19 R20 R21 R22 R23 | Resistor, small US symbol | R_Small_US | 10k | Digi-Key | 311-10.0KHRCT-ND | R_0603_1608Metric | RC0603FR-0710KL | 5
R2 R4 R6 R8 R10 R12 R14 R16 | Resistor, small US symbol | R_Small_US | 10.2k | Digi-Key | YAG1502CT-ND | R_0603_1608Metric | RT0603BRD0710K2L | 8
R18 | Resistor, small US symbol | R_Small_US | 44.2k | Digi-Key | YAG1662CT-ND | R_0603_1608Metric | RT0603BRD0744K2L | 1
R17 | Resistor, small US symbol | R_Small_US | 162k | Digi-Key | YAG1541CT-ND | R_0603_1608Metric | RT0603BRD07162KL | 1
U3 | 8-Channel, 24-bit, Simultaneous Sampling ADC, WQFN-64 (LFCSP-64) | AD7770 | AD7770 | Digi-Key | 505-AD7770ACPZ-ND | LFCSP-64-1EP_9x9mm_P0.5mm_EP5.21x5.21mm_LeadsExtended |  | 1
U4 | SPI EEPROM, 256Kb (32K x 8), No Identification Page, 2.5 to 5.5V, SO8 | M95256-WMN6P | M95320-RMN6 | Digi-Key | 497-15178-1-ND | SOIC-8_3.9x4.9mm_P1.27mm |  | 1
U1 | High output current, Rail-to-Rail Input/Output, 3MHz GBW, Operational Amplifiers, integrated RFI/EMI filter, 1.5V to 5.5V supply, SOT-23-5 | OPA310xDBV | OPA310xDBV | Digi-Key | 296-OPA310IDBVRCT-ND | SOT-23-5 |  | 1
U2 | 150mA Low Dropout Voltage Regulator, Fixed Output 3.3V, SOT-23-5 | TLV71333PDBV | TLV71333PDBV | Digi-Key | 296-35591-1-ND | SOT-23-5 |  | 1

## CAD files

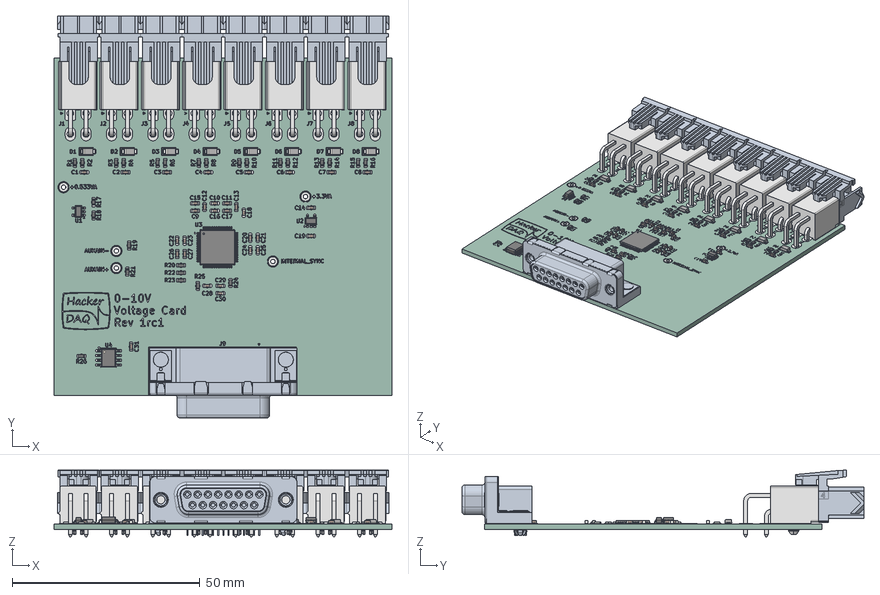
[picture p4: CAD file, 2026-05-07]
hardware/Exports/Voltage Card Rev 1rc1/cad/HackerDAQ Voltage Card.step
90.0 x 107.2 x 17.8 mm
C_0603_1608Metric x 31
R_0603_1608Metric x 26
D_SMF x 8
sLD15S33E4GX00LF
SOIC-8_3.9x4.9mm_P1.27mm
SOT-23-5 x 2
CP_64_15_ADI
kibot_b4m23kx4_pad
kibot_b4m23kx4_silkscreen x 2
kibot_b4m23kx4_PCB

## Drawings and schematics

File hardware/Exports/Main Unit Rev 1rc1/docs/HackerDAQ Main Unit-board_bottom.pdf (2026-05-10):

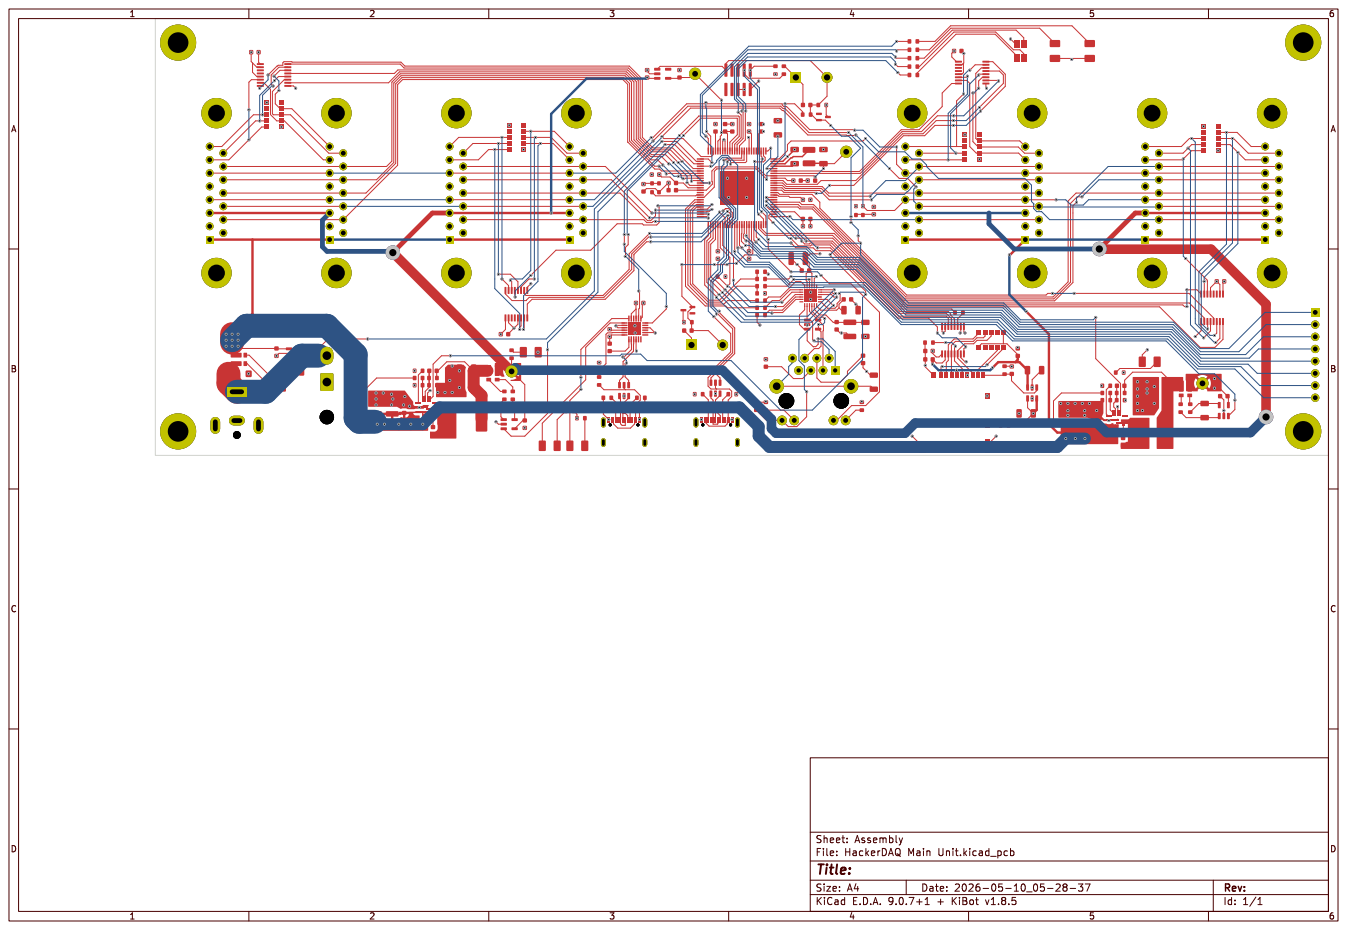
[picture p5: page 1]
Size: A4; Rev:; Date: 2026-05-10_05-28-37

Sheet: Assembly
File: HackerDAQ Main Unit.kicad_pcb
Title:
KiCad E.D.A. 9.0.7+1 + KiBot v1.8.5

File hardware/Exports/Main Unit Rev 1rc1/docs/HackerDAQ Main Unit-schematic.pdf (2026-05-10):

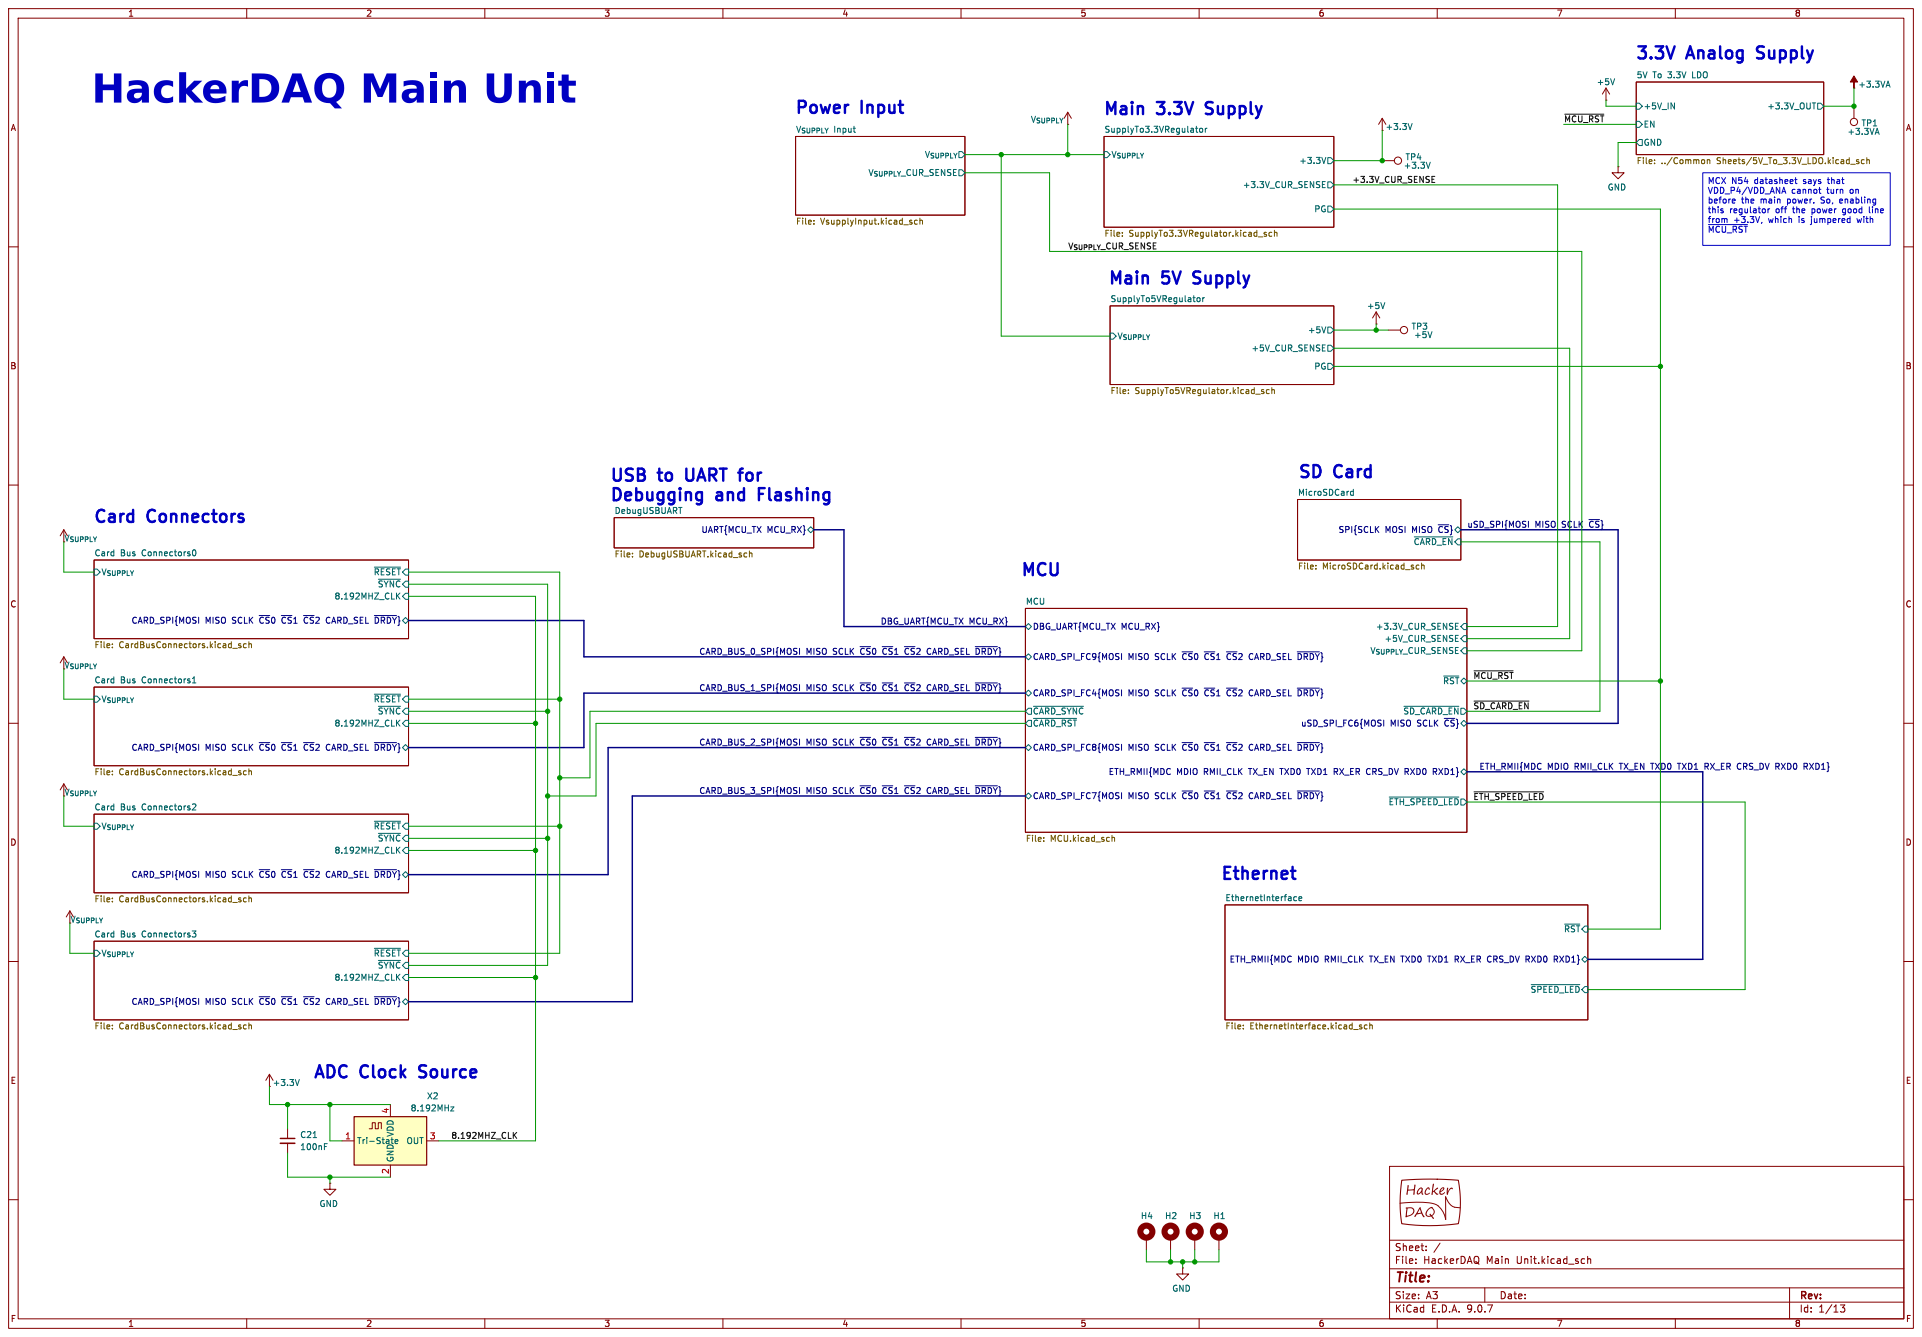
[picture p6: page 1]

V_{SUPPLY} Input File: VsupplyInput.kicad_sch

before the main power. So, enabling

USB to UART for
Debugging and Flashing
DebugUSBUART

SPI{SCLK MOSI MISO ~{CS}} MicroSDCard File: MicroSDCard.kicad_sch ETH_RMII{MDC MDIO RMII_CLK TX_EN TXD0 TXD1 RX_ER CRS_DV RXD0 RXD1}

uSD_SPI{MOSI MISO SCLK ~{CS}}

DBG_UART{MCU_TX MCU_RX}
+5V_CUR_SENSE CARD_SPI_FC7{MOSI MISO SCLK ~{CS}0~{CS}1~{CS}2CARD_SEL ~{DRDY}}
CARD_SPI_FC9{MOSI MISO SCLK ~{CS}0~{CS}1~{CS}2CARD_SEL ~{DRDY}}

CARD_BUS_1_SPI{MOSI MISO SCLK ~{CS}0~{CS}1~{CS}2CARD_SEL ~{DRDY}}

CARD_SPI_FC4{MOSI MISO SCLK ~{CS}0~{CS}1~{CS}2CARD_SEL ~{DRDY}}
~{CARD_SYNC}
~{CARD_RST}

uSD_SPI_FC6{MOSI MISO SCLK ~{CS}}

CARD_BUS_2_SPI{MOSI MISO SCLK ~{CS}0~{CS}1~{CS}2CARD_SEL ~{DRDY}}

CARD_SPI_FC8{MOSI MISO SCLK ~{CS}0~{CS}1~{CS}2CARD_SEL ~{DRDY}}

CARD_BUS_3_SPI{MOSI MISO SCLK ~{CS}0~{CS}1~{CS}2CARD_SEL ~{DRDY}}

V_{SUPPLY}
~{SYNC} 8.192MHZ_CLK CARD_SPI{MOSI MISO SCLK ~{CS}0~{CS}1~{CS}2CARD_SEL ~{DRDY}} Card Bus Connectors2 File: CardBusConnectors.kicad_sch

~{RST} EthernetInterface File: EthernetInterface.kicad_sch

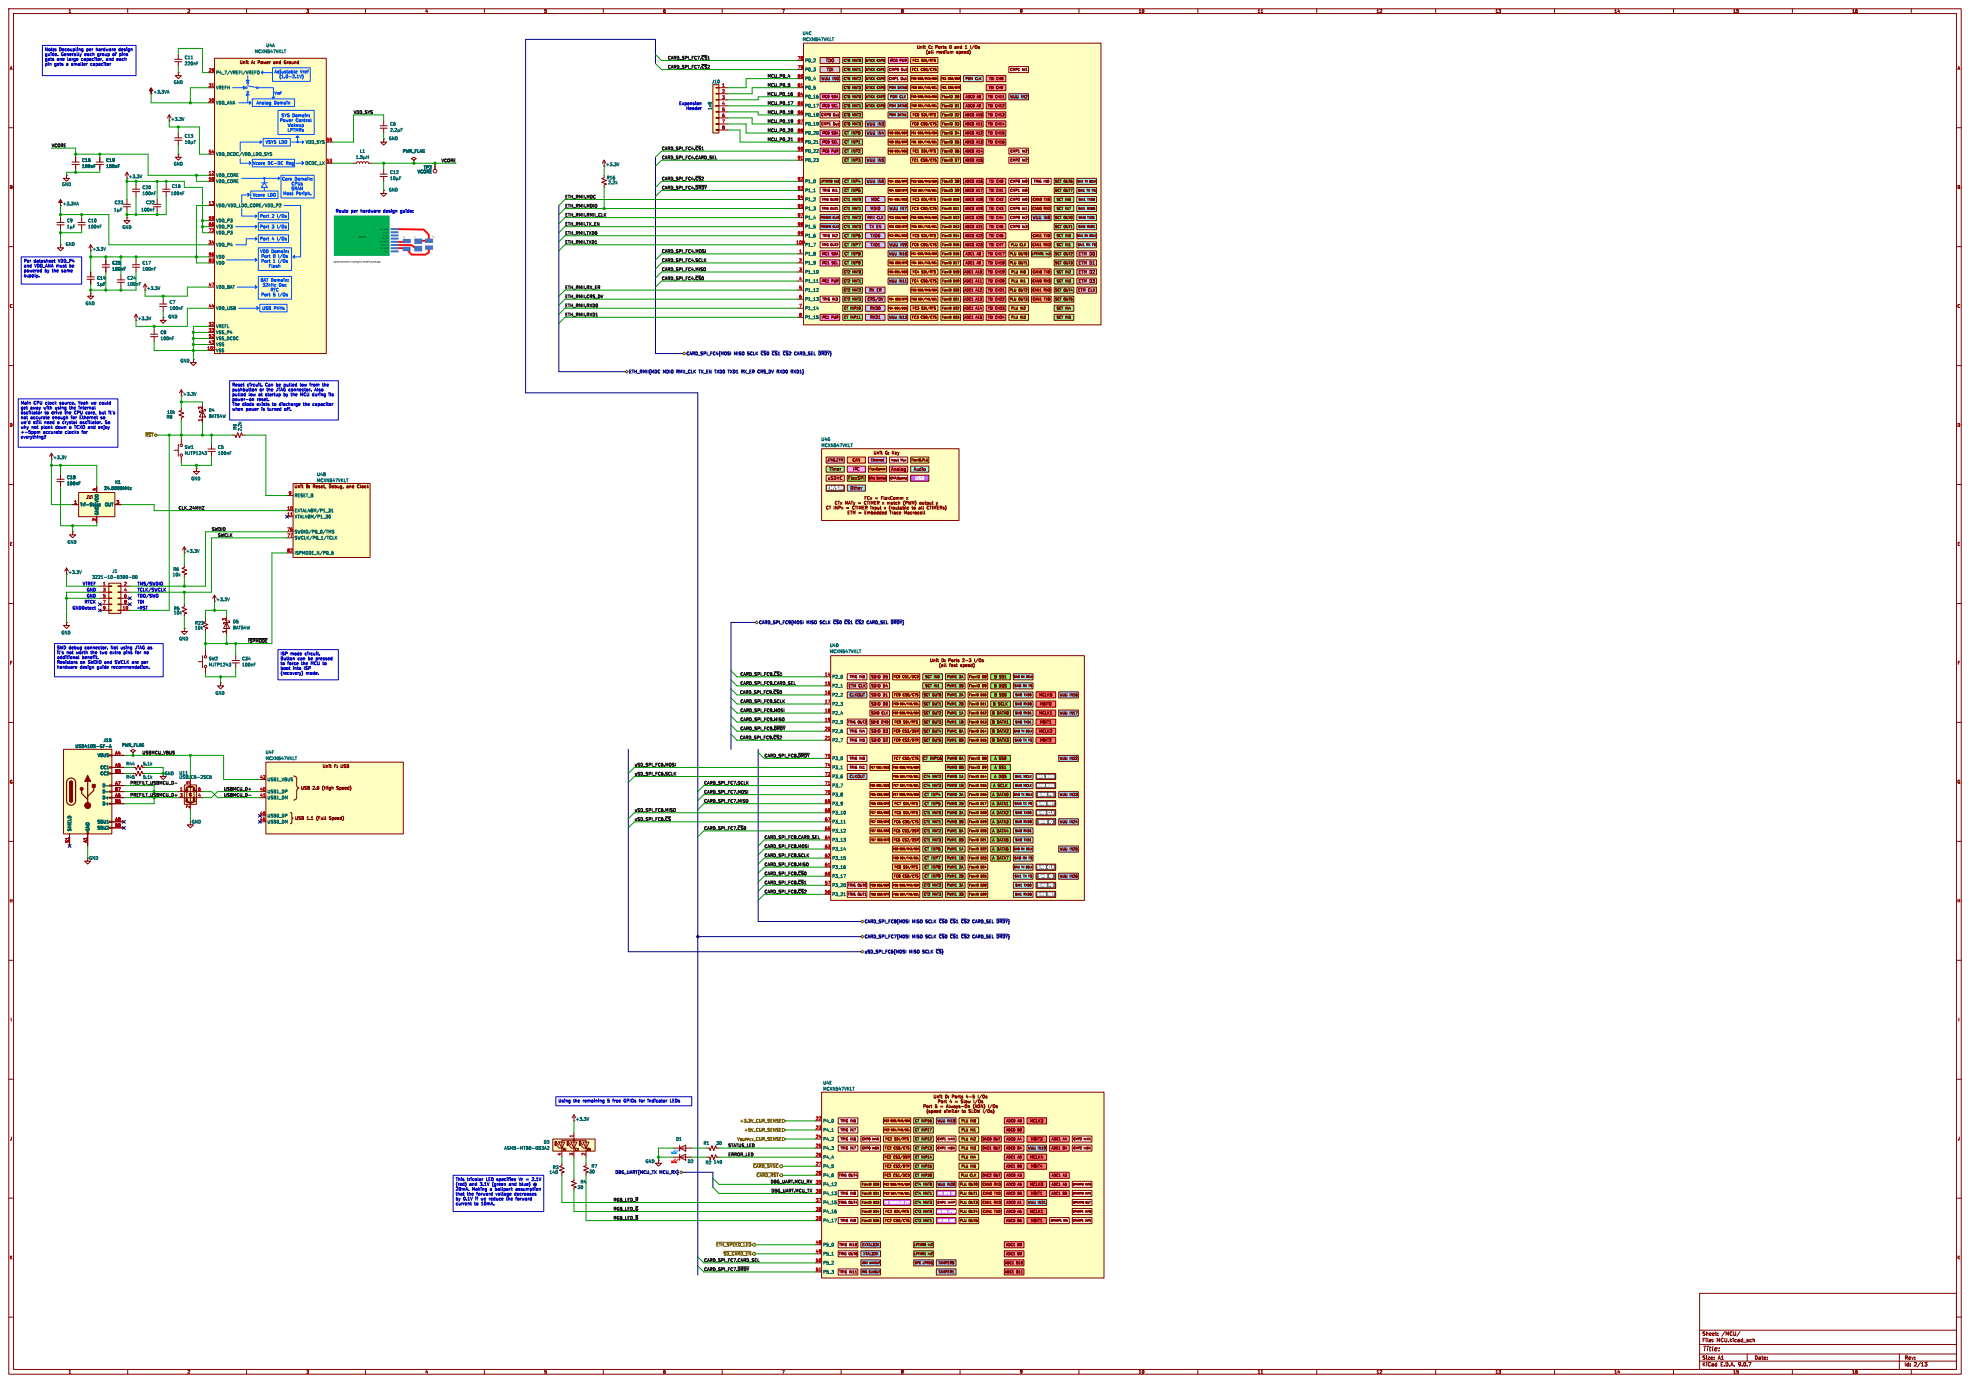
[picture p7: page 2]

Unit A: Power and Ground Analog Domain Vcore DC-DC Reg Port 2 I/Os Port 3 I/Os Port 4 I/Os USB PHYs VDD Domain:

Unit C: Ports 0 and 1 I/Os
CT0 MAT0 CT0 MAT1 CT0 MAT2 CT0 MAT3 CT0 MAT0 CT0 MAT1 CT0 MAT2 CT0 MAT3 CT INP0 CT INP1 CT INP2 CT INP3 CT INP4 CT INP5 CT1 MAT0 CT1 MAT1 CT1 MAT2 CT1 MAT3 CT INP6 CT INP7 CT INP8 CT INP9 CT2 MAT0 CT2 MAT1 CT2 MAT2 CT2 MAT3 CT INP10 CT INP11
UTICK CAP0 UTICK CAP1 UTICK CAP2 UTICK CAP3 UTICK CAP2 UTICK CAP3 WUU IN3 WUU IN4 WUU IN5 WUU IN6 MDC MDIO

CMP0 Out PDM DATA0 PDM CLK

FC0 SCK/TXD/SCL FC0 SDO/RXD/SDA

FC0 SCK/TXD/SCL FC0 SDI/RTS

FC1 SCK/TXD/SCL FC1 SDI/RTS

FC3 SDO/RXD/SDA
FlexIO D10 FlexIO D11 FlexIO D12 FlexIO D13 FlexIO D14 FlexIO D15 FlexIO D16 FlexIO D17 FlexIO D18 FlexIO D19 FlexIO D20 FlexIO D21 FlexIO D22 FlexIO D23

LPTMR1 In3 TRIG IN0 CAN0 TXD
SAI1 TXD0 SAI1 RXD0 SAI0 TXD1 SAI0 RXD1 SAI1 RX BCLK SAI1 RX FS ETM D0 ETM D1 ETM D2 ETM D3 ETM CLK

SCT OUT6 SCT OUT7 SCT IN6 SCT IN7 SCT OUT0 SCT OUT1 SCT IN0 SCT IN1 SCT OUT2 SCT OUT3 SCT IN2 SCT IN3 SCT OUT4 SCT OUT5 SCT IN4 SCT IN5

SAI1 TX BCLK SAI1 TX FS

FC3 SCK/TXD/SCL FC3 SDI/RTS

Route per hardware design guide:

RMII CLK TX EN
TXD0 TXD1 RX ER

FC5 SCK/TXD/SCL FC5 SDI/RTS

CAN1 RXD
PLU OUT0 PLU OUT1 PLU IN0 PLU IN1 PLU OUT2 PLU OUT3 PLU IN2 PLU IN3

FC4 SCK/TXD/SCL FC4 SDI/RTS

and VDD_ANA must be
powered by the same
supply.

CARD_SPI_FC4{MOSI MISO SCLK ~{CS}0~{CS}1~{CS}2CARD_SEL ~{DRDY}}

Main CPU clock source. Yeah we could

Sinc Demod Unit G: Key

ETM = Embedded Trace Macrocell JTAG,ETM
Timer uSDHC

Unit B: Reset, Debug, and Clock RESET_B 9 EXTAL48M/P1_31 10 XTAL48M/P1_30 11 SWDIO/P0_0/TMS 76 SWCLK/P0_1/TCLK 77

CTx MATy = CTIMER x match (PWM) output y

CARD_SPI_FC9{MOSI MISO SCLK ~{CS}0~{CS}1~{CS}2CARD_SEL ~{DRDY}}
CARD_SPI_FC9.CARD_SEL CARD_SPI_FC8.MISO
CARD_SPI_FC9.~{CS}0
CARD_SPI_FC8.MOSI CARD_SPI_FC9.SCLK

it's not worth the two extra pins for no

ISP mode circuit. Button can be pressed

to force the MCU to
boot into ISP

SDIO D5 SDIO D4 SDIO D1 SDIO D0 SDIO CLK
SCT IN0 SCT IN1 SCT OUT0 SCT OUT1 SCT OUT2 SCT OUT3 SCT OUT4 SCT OUT5 CT INP16 CT4 MAT2 CT4 MAT3 CT INP4 CT INP5 CT1 MAT0 CT1 MAT1 CT1 MAT2 CT1 MAT3 CT INP6 CT INP7 CT INP8 CT INP9 CT2 MAT2 CT2 MAT3
SAI0 TXD0 SAI0 RXD0 SAI0 RXD1 SAI0 TXD1 SAI0 TX BCLK SAI0 TX FS

FlexIO D10 FlexIO D11 FlexIO D12 FlexIO D13 FlexIO D14 FlexIO D15 FlexIO D8 FlexIO D9

TRIG IN5 ETM CLK CLKOUT

SAI0 RX BCLK SAI0 RX FS

FC9 SCK/TXD/SCL FC9 SDO/RXD/SDA FC9 SDI/RTS

SDIO CMD SDIO D3 SDIO D2

USB 1.1 (Full Speed) USB 2.0 (High Speed) Unit F: USB USB1_VBUS 42 USB1_DP 40 USB1_DM 41 USB0_DP 46 USB0_DM 45 U4F MCXN547VKLT

FC6 SCK/TXD/SCL FC7 SCK/TXD/SCL FC7 SDO/RXD/SDA FC7 SDI/RTS

SAI1 MCLK
SAI0 TXD0 SAI0 RXD0 SAI0 RXD1 SAI0 TXD1 SAI0 RX BCLK SAI0 RX FS

SAI0 TX BCLK SAI0 TX FS

FC8 SCK/TXD/SCL FC8 SDI/RTS

CARD_SPI_FC8{MOSI MISO SCLK ~{CS}0~{CS}1~{CS}2CARD_SEL ~{DRDY}}

CARD_SPI_FC7{MOSI MISO SCLK ~{CS}0~{CS}1~{CS}2CARD_SEL ~{DRDY}}

uSD_SPI_FC6{MOSI MISO SCLK ~{CS}}

OPAMP0 INP0 OPAMP0 INP1 OPAMP0 OUT OPAMP1 INP0 OPAMP1 INP1 P4_0 22 P4_1 23 P4_2 24 P4_3 25 P4_4 26 P4_5 27 P4_6 28 P4_12 35 P4_13 36 P4_15 37 P4_16 38 P4_17 39 P5_0 48 P5_1 49 P5_2 50 P5_3 51 U4E MCXN547VKLT
PLU OUT0 PLU OUT1 PLU OUT3 PLU OUT4 PLU OUT5 DAC0 OUT DAC1 OUT DAC2 OUT CAN0 RXD

CMP1 In4P WUU IN18 WUU IN20 HS OTG ID

FC2 SCK/TXD/SCL FC2 SDI/RTS
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

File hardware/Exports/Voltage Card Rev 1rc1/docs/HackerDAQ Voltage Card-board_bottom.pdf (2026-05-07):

Ch7 | Ch4 | Ch1
Ch2 | Ch0

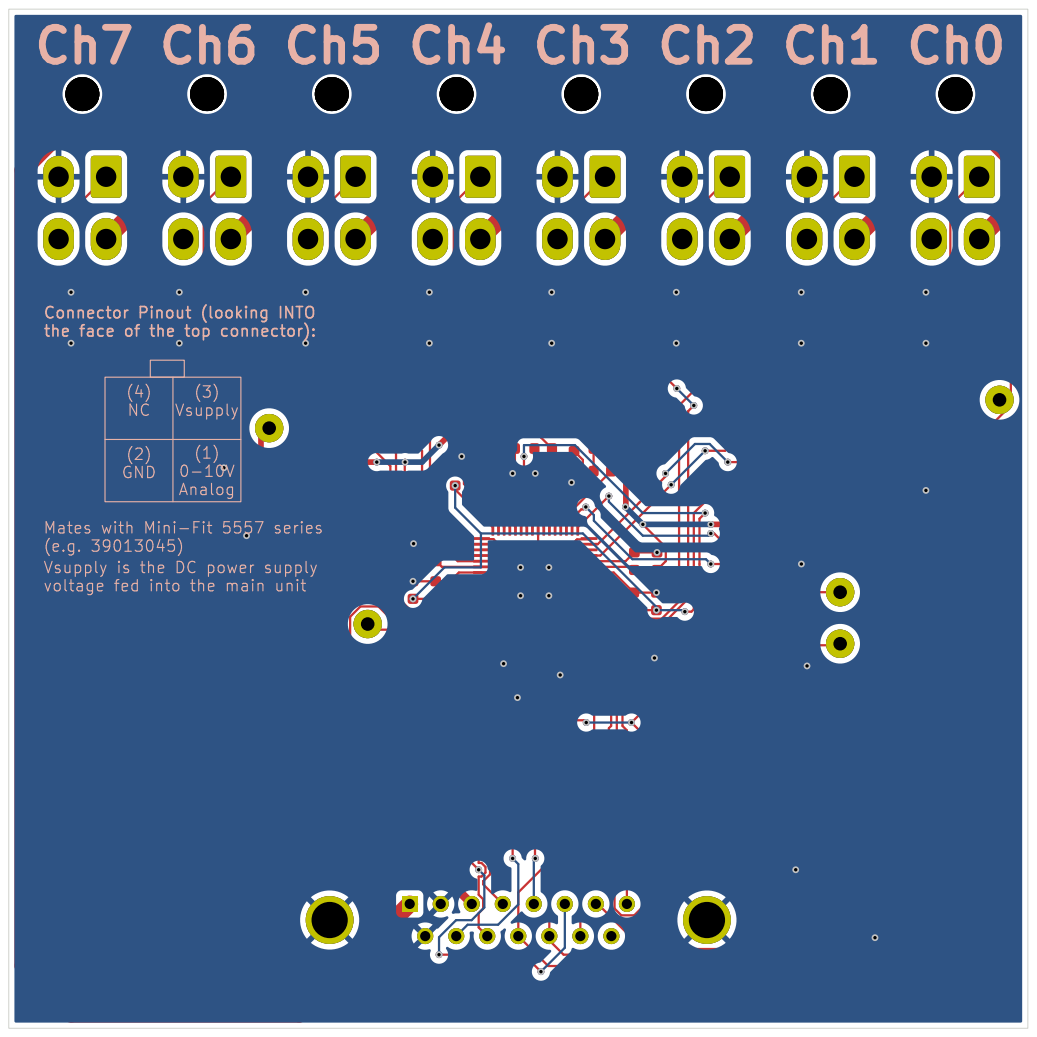
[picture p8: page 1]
Sheet: Assembly; File:; HackerDAQ Voltage Card.kicad_pcb; Title:; Size: A4; Rev:; KiCad; E.D.A. 9.0.7+1 + KiBot v1.8.5; Date: 2026-05-07_05-04-41; Vsupply; Connector Pinout; (looking INTO; Vsupply is the DC power; supply; Mates with Mini-Fit 5557; series; GND; Analog

the face of the top connector):

voltage fed into the main unit

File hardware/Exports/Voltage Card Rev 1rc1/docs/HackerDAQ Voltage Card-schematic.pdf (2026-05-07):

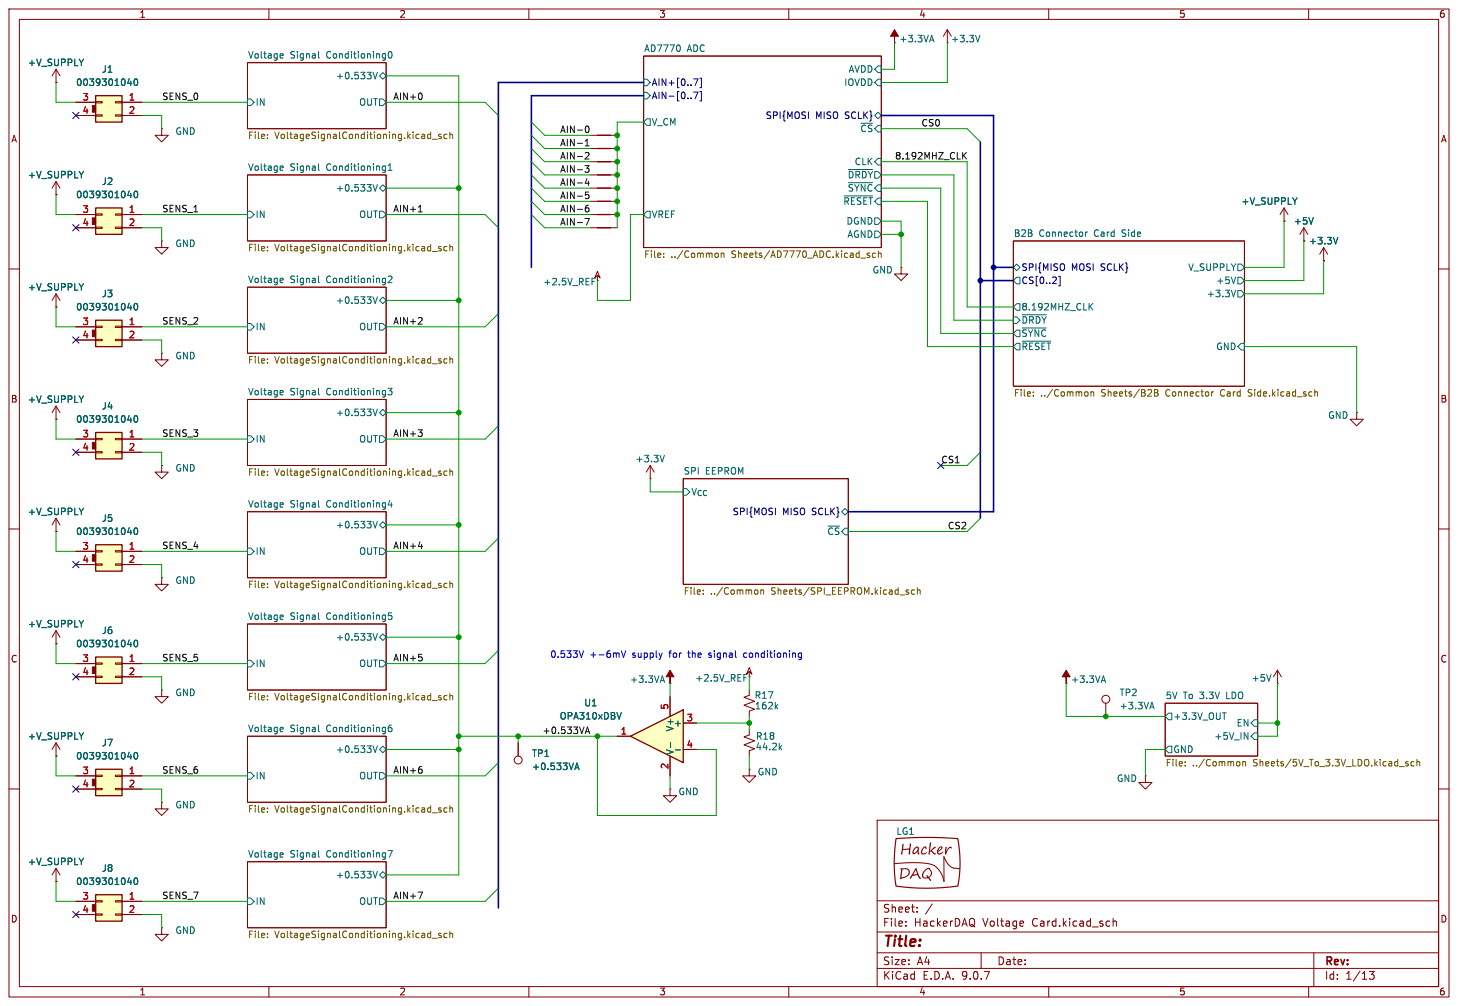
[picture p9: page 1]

AIN+[0..7]
AIN-[0..7] V_CM
SPI{MOSI MISO SCLK} VREF

SPI{MISO MOSI SCLK}

SPI{MOSI MISO SCLK}

Id: 1/13 Title: File: HackerDAQ Voltage Card.kicad_sch Sheet: /

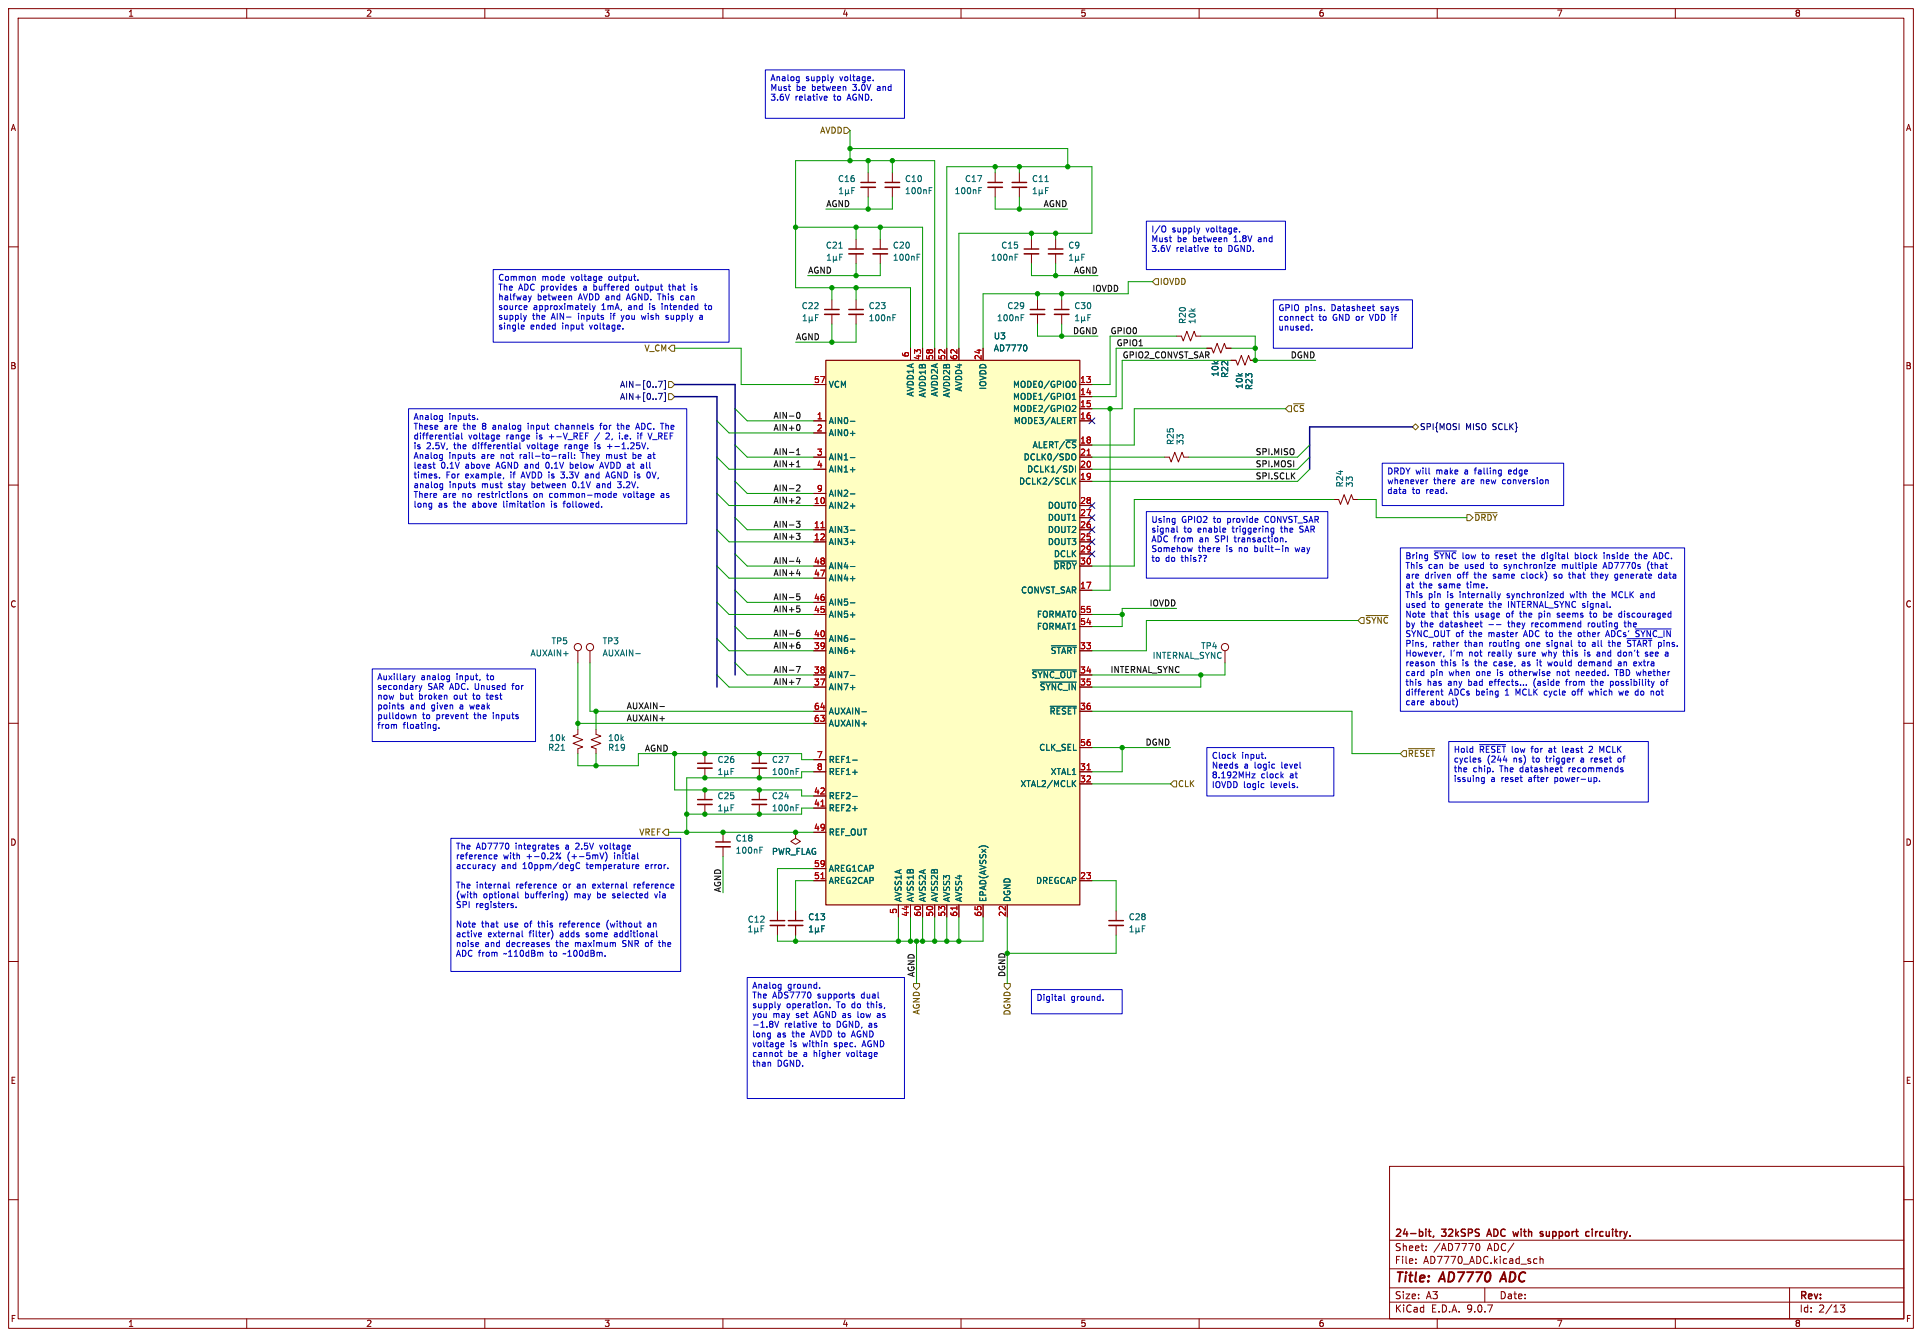
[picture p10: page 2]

Analog supply voltage. Must be between 3.0V and
AGND

I/O supply voltage. Must be between 1.8V and

IOVDD
to do this?? Digital ground.

supply the AIN- inputs if you wish supply a
single ended input voltage.

6 AVSS1B 44 AVDD1B 43 AVSS2A 60 AVDD2A 58 AVSS2B 50 AVDD2B 52 AVSS3 53 AVDD4 62 AVSS4 61 IOVDD 24 EPAD(AVSSx) 65 DGND 22 MODE0/GPIO0 13 MODE1/GPIO1 14 MODE2/GPIO2 15 MODE3/ALERT 16 ALERT/~{CS}18 DCLK0/SDO 21 DCLK1/SDI 20 DCLK2/SCLK 19 DOUT0 28 DOUT1 27 DOUT2 26 DOUT3 25 DCLK 29 ~{DRDY} 30 CONVST_SAR 17 FORMAT0 55 FORMAT1 54 ~{START} 33 ~{SYNC_OUT} 34 ~{SYNC_IN}35 ~{RESET} 36 CLK_SEL 56 XTAL1 31 XTAL2/MCLK 32 DREGCAP 23

6 AVSS1B 44 AVDD1B 43 AVSS2A 60 AVDD2A 58 AVSS2B 50 AVDD2B 52 AVSS3 53 AVDD4 62 AVSS4 61 IOVDD 24 EPAD(AVSSx) 65 DGND 22 MODE0/GPIO0 13 MODE1/GPIO1 14 MODE2/GPIO2 15 MODE3/ALERT 16 ALERT/~{CS}18 DCLK0/SDO 21 DCLK1/SDI 20 DCLK2/SCLK 19 DOUT0 28 DOUT1 27 DOUT2 26 DOUT3 25 DCLK 29 ~{DRDY} 30 CONVST_SAR 17 FORMAT0 55 FORMAT1 54 ~{START} 33 ~{SYNC_OUT} 34 ~{SYNC_IN}35 ~{RESET} 36 CLK_SEL 56 XTAL1 31 XTAL2/MCLK 32 DREGCAP 23 10k R2310k R22

SPI{MOSI MISO SCLK} DGND

~{DRDY} CLK
IOVDD logic levels. Using GPIO2 to provide CONVST_SAR

used to generate the INTERNAL_SYNC signal. Note that this usage of the pin seems to be discouraged

reason this is the case, as it would demand an extra

cycles (244 ns) to trigger a reset of

long as the AVDD to AGND
voltage is within spec. AGND
cannot be a higher voltage

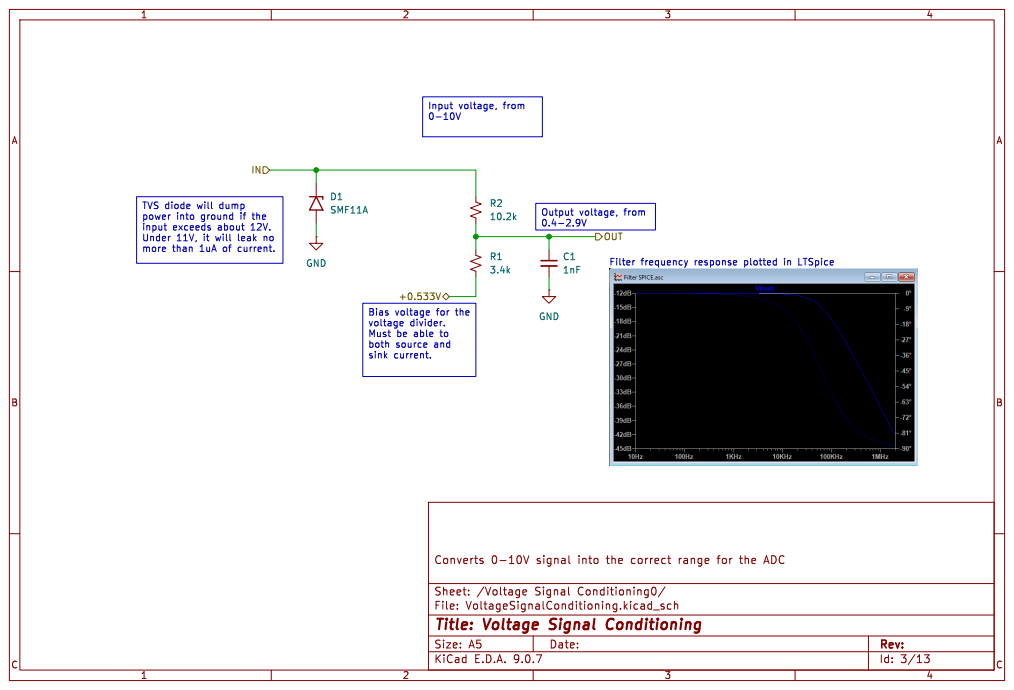
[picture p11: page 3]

TVS diode will dump
power into ground if the

Bias voltage for the
voltage divider. Must be able to

Id: 3/13 Title: Voltage Signal Conditioning

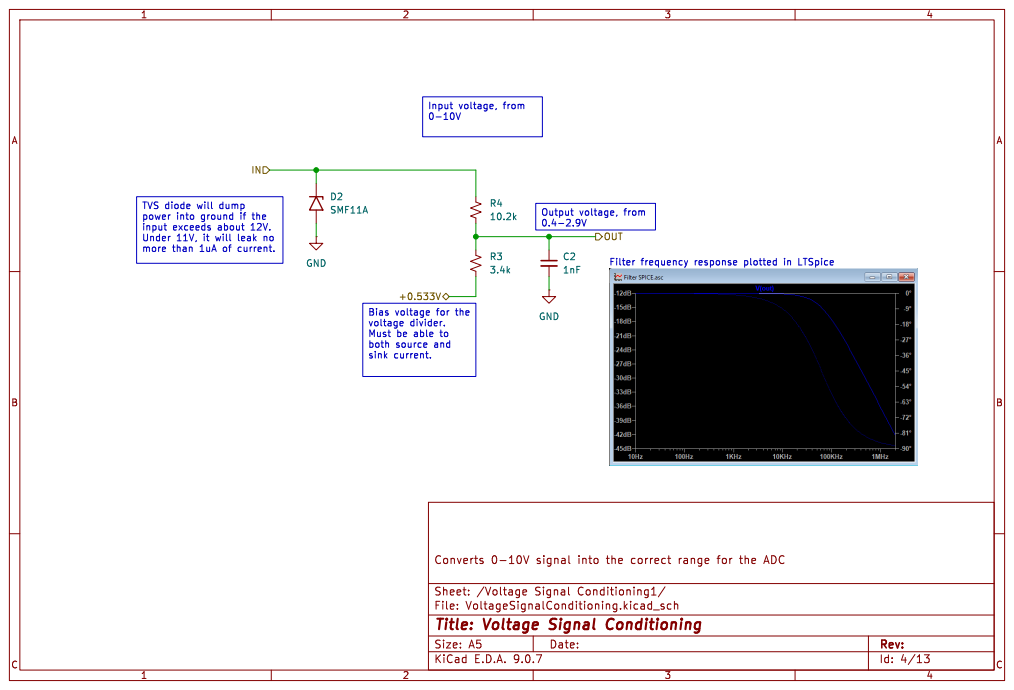
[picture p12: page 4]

TVS diode will dump
power into ground if the

Bias voltage for the
voltage divider. Must be able to

Id: 4/13 Title: Voltage Signal Conditioning

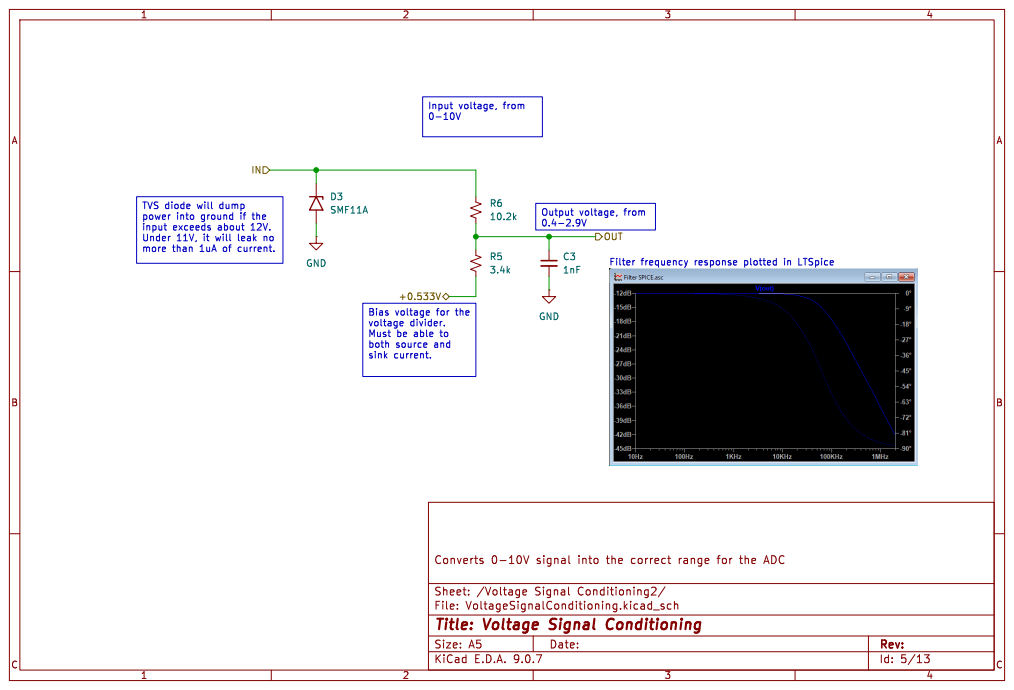
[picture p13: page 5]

TVS diode will dump
power into ground if the

Bias voltage for the
voltage divider. Must be able to

Id: 5/13 Title: Voltage Signal Conditioning

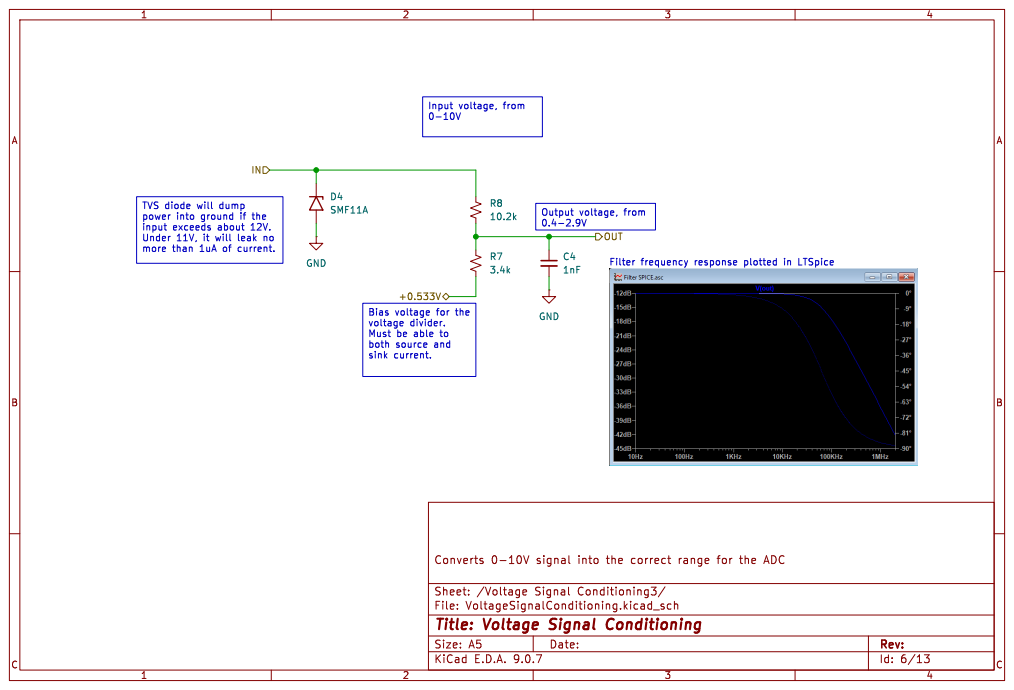
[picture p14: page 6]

TVS diode will dump
power into ground if the

Bias voltage for the
voltage divider. Must be able to

Id: 6/13 Title: Voltage Signal Conditioning

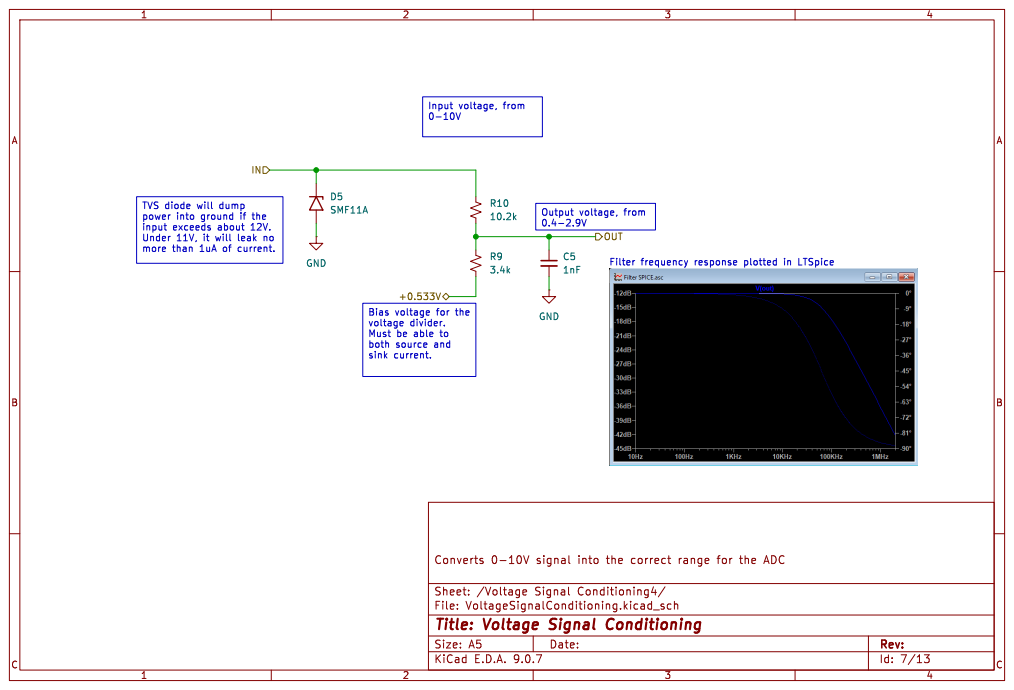
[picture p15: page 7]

TVS diode will dump
power into ground if the

Bias voltage for the
voltage divider. Must be able to

Id: 7/13 Title: Voltage Signal Conditioning

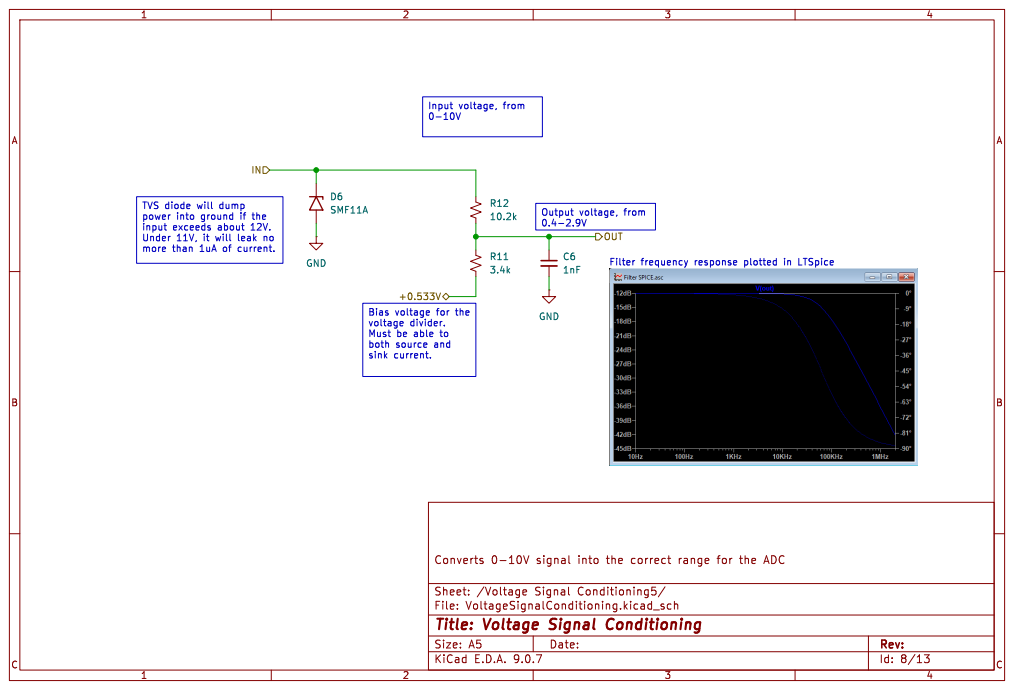
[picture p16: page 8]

TVS diode will dump
power into ground if the

Bias voltage for the
voltage divider. Must be able to

Id: 8/13 Title: Voltage Signal Conditioning


TVS diode will dump
power into ground if the

Bias voltage for the
voltage divider. Must be able to

Id: 9/13 Title: Voltage Signal Conditioning


TVS diode will dump
power into ground if the

Bias voltage for the
voltage divider. Must be able to

Id: 10/13 Title: Voltage Signal Conditioning


Id: 11/13 Title: 5V To 3.3V LDO


- Digital +5V and +3.3V rails from main board to card
- SPI (MOSI, MISO, SCLK)
- 3x chip selects
- 8.192MHz clock (for AD7770 ADC)
- Sync signal from main board to card
- Data ready signal from card to main board
- Reset line from main board to card

SPI{MISO MOSI SCLK}

Id: 12/13 Title: B2B Connector Card-Side


V_{CC} may be from

SPI{MOSI MISO SCLK}

SPI.MOSI HOLD and write protect not used, so ~{W}and ~{HOLD}tied

Id: 13/13 Title: SPI EEPROM


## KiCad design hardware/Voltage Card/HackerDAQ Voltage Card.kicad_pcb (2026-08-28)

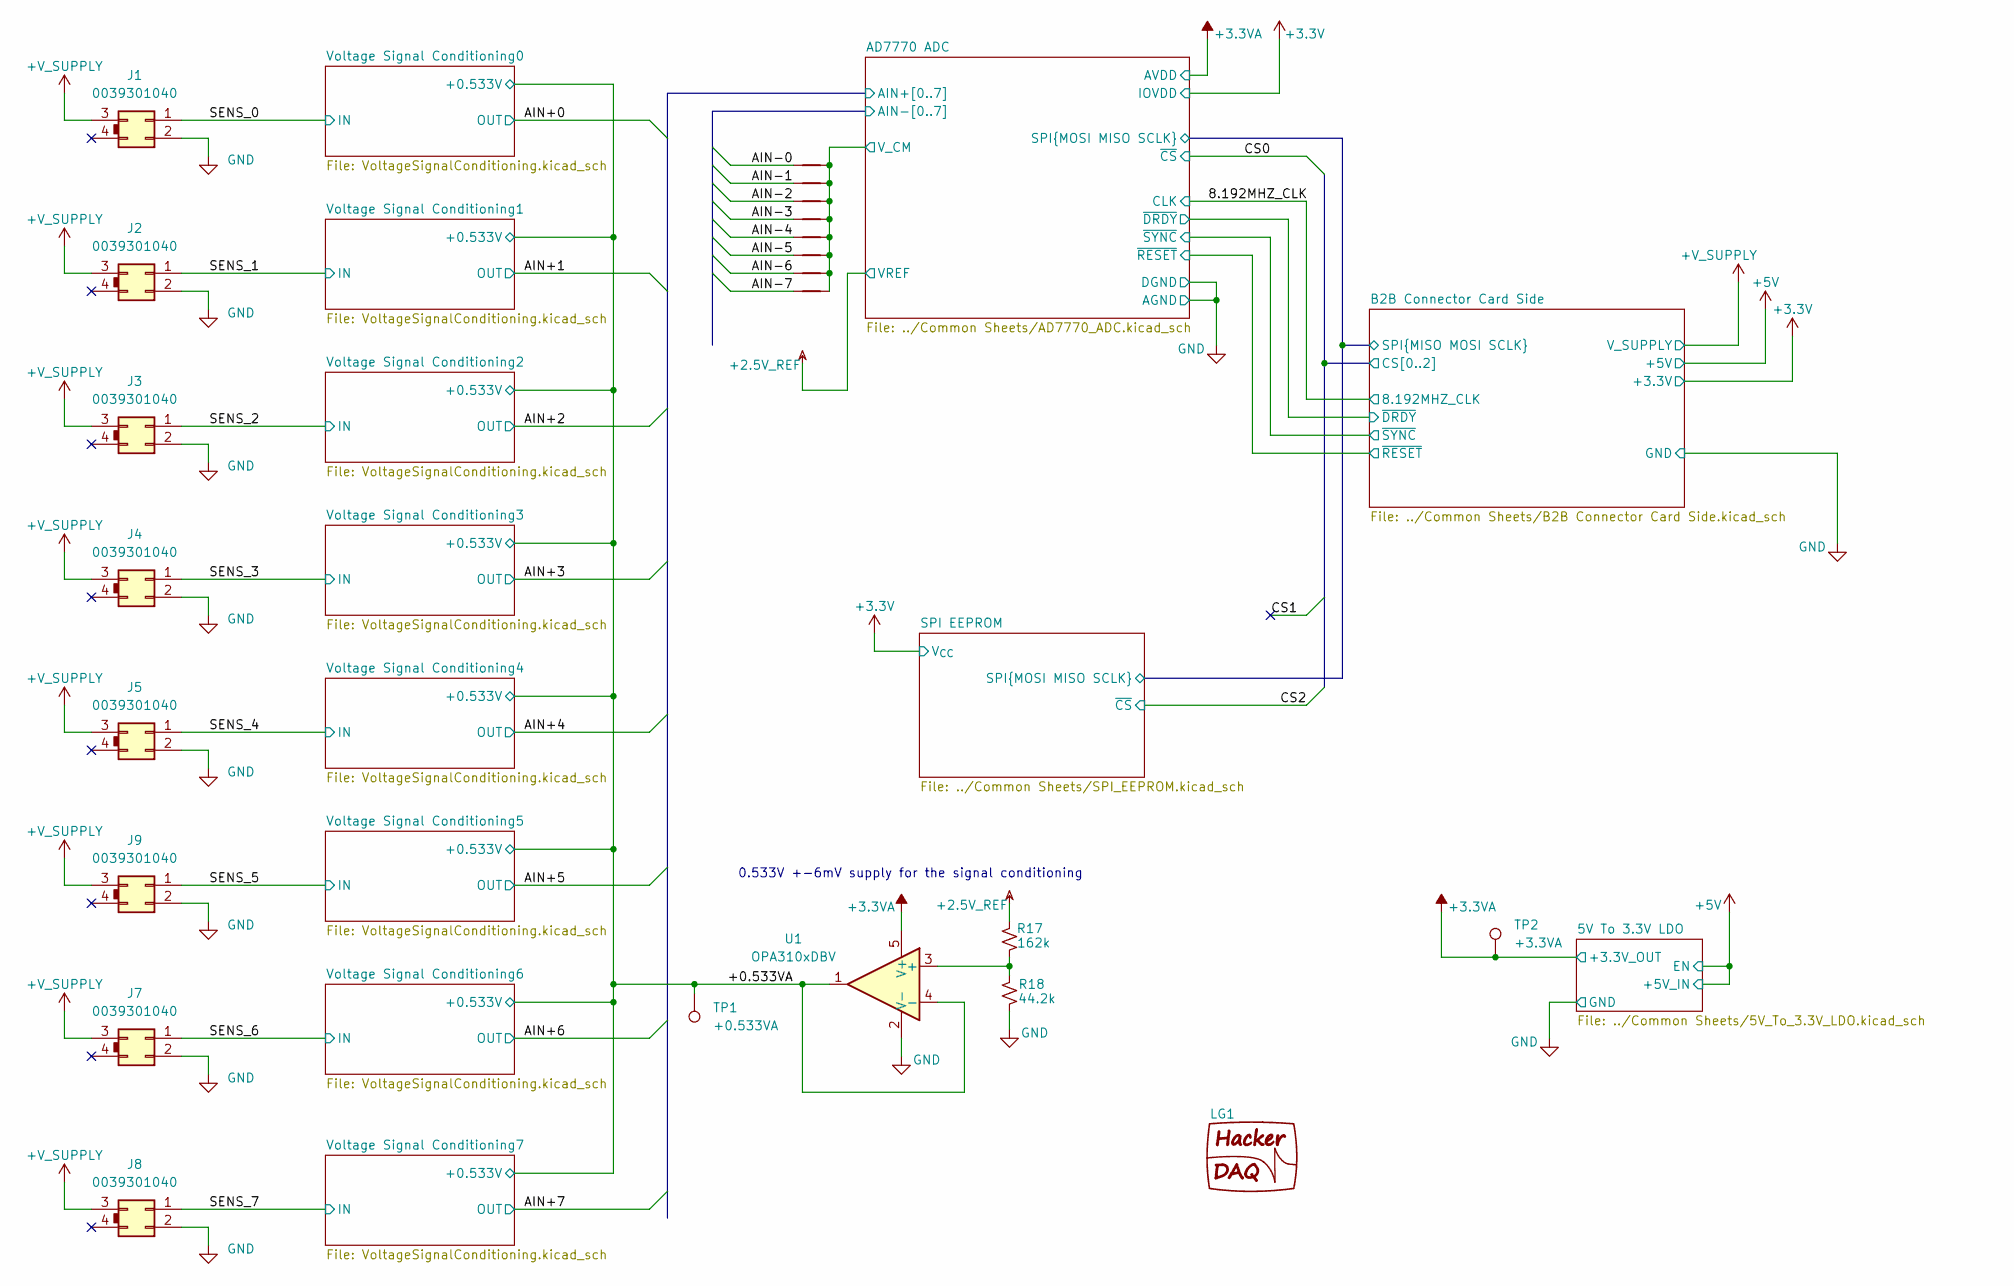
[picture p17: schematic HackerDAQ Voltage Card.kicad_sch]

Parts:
J1, J2, J3, J4, J5, J7, J8, J9: 0039301040; Molex_Mini-Fit_Jr_5569-04A2_2x02_P4.20mm_Horizontal
LG1: HackerDAQ Logo
NT1, NT2, NT3, NT4, NT5, NT6, NT7, NT8: NetTie_2; NetTie-2_SMD_Pad0.2mm
R17: 162k; R_0603_1608Metric
R18: 44.2k; R_0603_1608Metric
TP1: +0.533VA; TestPoint_THTPad_D2.5mm_Drill1.2mm
TP2: +3.3VA; TestPoint_THTPad_D2.5mm_Drill1.2mm
U1: OPA310xDBV; SOT-23-5

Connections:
+2.5V_REF: R17.1; also elsewhere on the board
+3.3VA: TP2.1, U1.5 (V+); also elsewhere on the board
+V_SUPPLY: J1.3, J2.3, J3.3, J4.3, J5.3, J7.3, J8.3, J9.3; also elsewhere on the board
/+0.533VA: TP1.1, U1.1, U1.4 (-); also elsewhere on the board
/AD7770 ADC/AIN-0: NT1.1; also elsewhere on the board
/AD7770 ADC/AIN-1: NT3.1; also elsewhere on the board
/AD7770 ADC/AIN-2: NT5.1; also elsewhere on the board
/AD7770 ADC/AIN-3: NT7.1; also elsewhere on the board
/AD7770 ADC/AIN-4: NT2.1; also elsewhere on the board
/AD7770 ADC/AIN-5: NT4.1; also elsewhere on the board
/AD7770 ADC/AIN-6: NT6.1; also elsewhere on the board
/AD7770 ADC/AIN-7: NT8.1; also elsewhere on the board
/AD7770 ADC/V_CM: NT1.2, NT2.2, NT3.2, NT4.2, NT5.2, NT6.2, NT7.2, NT8.2; also elsewhere on the board
/SENS_0: J1.1; also elsewhere on the board
/SENS_1: J2.1; also elsewhere on the board
/SENS_2: J3.1; also elsewhere on the board
/SENS_3: J4.1; also elsewhere on the board
/SENS_4: J5.1; also elsewhere on the board
/SENS_5: J9.1; also elsewhere on the board
/SENS_6: J7.1; also elsewhere on the board
/SENS_7: J8.1; also elsewhere on the board
GND: J1.2, J2.2, J3.2, J4.2, J5.2, J7.2, J8.2, J9.2, R18.2, U1.2 (V-); also elsewhere on the board
unnamed: R17.2, R18.1, U1.3 (+)

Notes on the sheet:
0.533V +-6mV supply for the signal conditioning

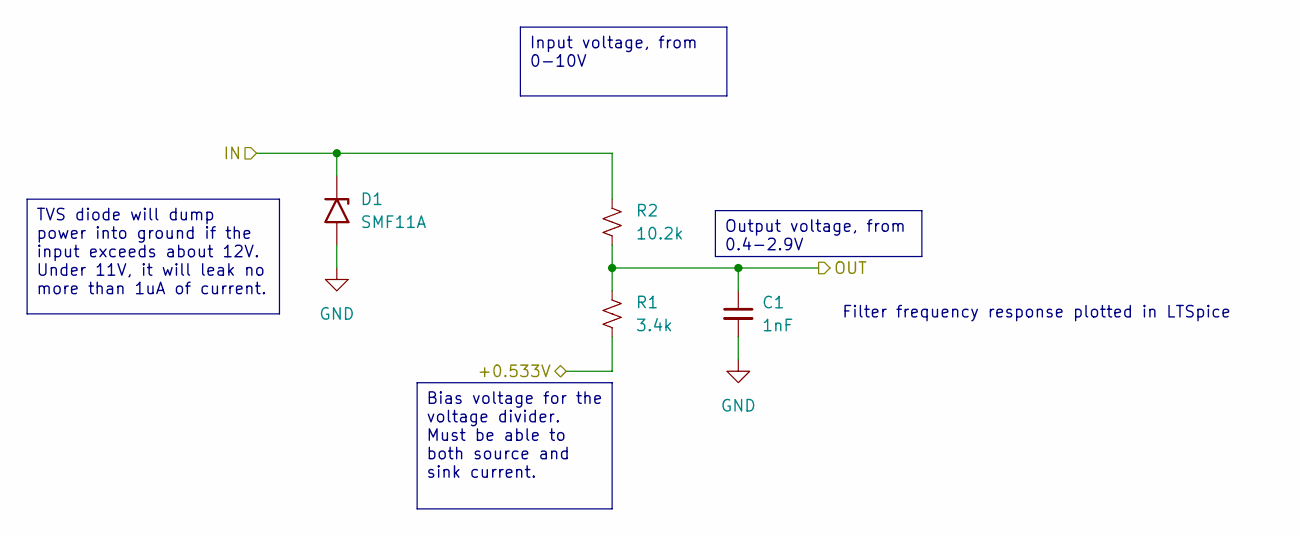
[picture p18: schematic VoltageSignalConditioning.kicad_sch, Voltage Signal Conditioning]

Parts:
C1: 1nF; C_0603_1608Metric
D1: SMF11A; D_SMF
R1: 3.4k; R_0603_1608Metric
R2: 10.2k; R_0603_1608Metric

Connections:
/+0.533VA: R1.2; also elsewhere on the board
/AD7770 ADC/AIN+0: C1.1, R1.1, R2.2; also elsewhere on the board
/SENS_0: D1.1 (A1), R2.1; also elsewhere on the board
GND: C1.2, D1.2 (A2); also elsewhere on the board

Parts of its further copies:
C2, C3, C4, C6, C7, C8, C31: 1nF; C_0603_1608Metric
D2, D3, D4, D5, D6, D7, D8: SMF11A; D_SMF
R3, R5, R7, R9, R11, R13, R15: 3.4k; R_0603_1608Metric
R4, R6, R8, R10, R12, R14, R16: 10.2k; R_0603_1608Metric

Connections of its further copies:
/+0.533VA: R3.2, R5.2, R7.2, R9.2, R11.2, R13.2, R15.2; also elsewhere on the board
/AD7770 ADC/AIN+1: C2.1, R3.1, R4.2; also elsewhere on the board
/AD7770 ADC/AIN+2: C3.1, R5.1, R6.2; also elsewhere on the board
/AD7770 ADC/AIN+3: C4.1, R7.1, R8.2; also elsewhere on the board
/AD7770 ADC/AIN+4: C31.1, R9.1, R10.2; also elsewhere on the board
/AD7770 ADC/AIN+5: C6.1, R11.1, R12.2; also elsewhere on the board
/AD7770 ADC/AIN+6: C7.1, R13.1, R14.2; also elsewhere on the board
/AD7770 ADC/AIN+7: C8.1, R15.1, R16.2; also elsewhere on the board
/SENS_1: D2.1 (A1), R4.1; also elsewhere on the board
/SENS_2: D3.1 (A1), R6.1; also elsewhere on the board
/SENS_3: D4.1 (A1), R8.1; also elsewhere on the board
/SENS_4: D5.1 (A1), R10.1; also elsewhere on the board
/SENS_5: D6.1 (A1), R12.1; also elsewhere on the board
/SENS_6: D7.1 (A1), R14.1; also elsewhere on the board
/SENS_7: D8.1 (A1), R16.1; also elsewhere on the board
GND: C2.2, C3.2, C4.2, C6.2, C7.2, C8.2, C31.2, D2.2 (A2), D3.2 (A2), D4.2 (A2), D5.2 (A2), D6.2 (A2), D7.2 (A2), D8.2 (A2); also elsewhere on the board

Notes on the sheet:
Filter frequency response plotted in LTSpice
Output voltage, from 0.4-2.9V
Input voltage, from 0-10V
Bias voltage for the voltage divider. Must be able to both source and sink current.
TVS diode will dump power into ground if the input exceeds about 12V. Under 11V, it will leak no more than 1uA of current.

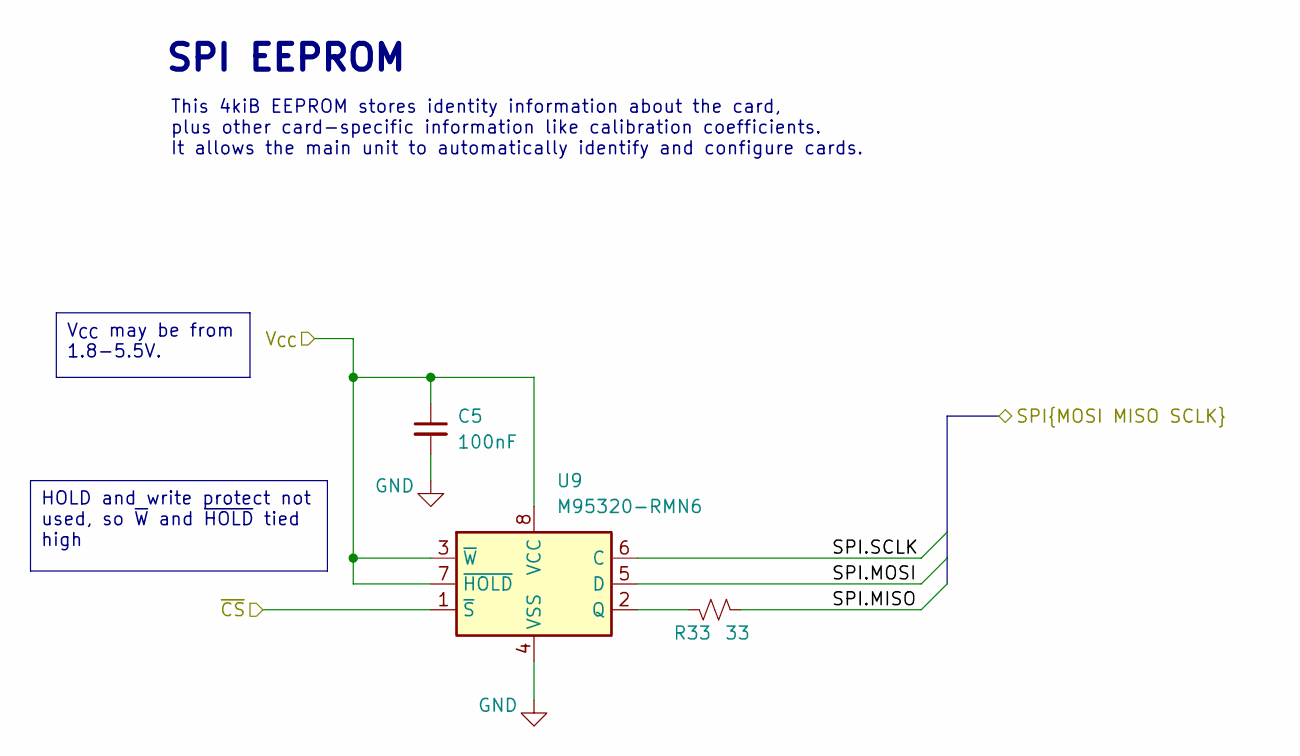
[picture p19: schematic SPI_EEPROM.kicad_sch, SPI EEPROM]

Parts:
C5: 100nF; C_0603_1608Metric
R33: 33; R_0603_1608Metric
U9: M95320-RMN6; SOIC-8_3.9x4.9mm_P1.27mm

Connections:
+3.3V: C5.1, U9.3 (~W), U9.7 (~HOLD), U9.8 (VCC); also elsewhere on the board
/AD7770 ADC/SPI.MISO: R33.2; also elsewhere on the board
/AD7770 ADC/SPI.MOSI: U9.5 (D); also elsewhere on the board
/AD7770 ADC/SPI.SCLK: U9.6 (C); also elsewhere on the board
/B2B Connector Card Side/CS2: U9.1 (~S); also elsewhere on the board
GND: C5.2, U9.4 (VSS); also elsewhere on the board
unnamed: R33.1, U9.2 (Q)

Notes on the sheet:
SPI EEPROM
This 4kiB EEPROM stores identity information about the card, plus other card-specific information like calibration coefficients. It allows the main unit to automatically identify and configure cards.
HOLD and write protect not used, so ~{W} and ~{HOLD} tied high
V_{CC} may be from 1.8-5.5V.

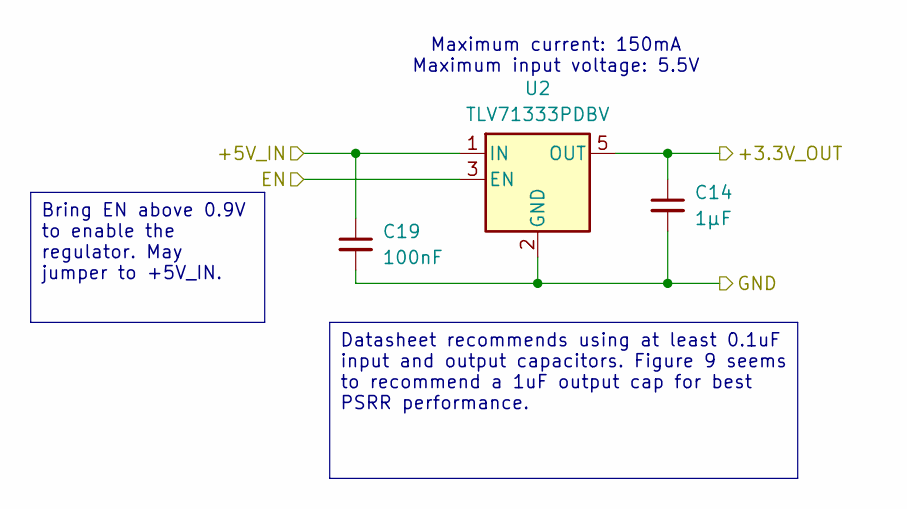
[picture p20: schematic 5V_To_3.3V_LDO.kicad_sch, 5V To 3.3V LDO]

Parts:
C14: 1µF; C_0603_1608Metric
C19: 100nF; C_0603_1608Metric
U2: TLV71333PDBV; SOT-23-5

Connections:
+3.3VA: C14.1, U2.5 (OUT); also elsewhere on the board
+5V: C19.1, U2.1 (IN), U2.3 (EN); also elsewhere on the board
GND: C14.2, C19.2, U2.2 (GND); also elsewhere on the board

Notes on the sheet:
Maximum current: 150mA Maximum input voltage: 5.5V
Bring EN above 0.9V to enable the regulator. May jumper to +5V_IN.
Datasheet recommends using at least 0.1uF input and output capacitors. Figure 9 seems to recommend a 1uF output cap for best PSRR performance.

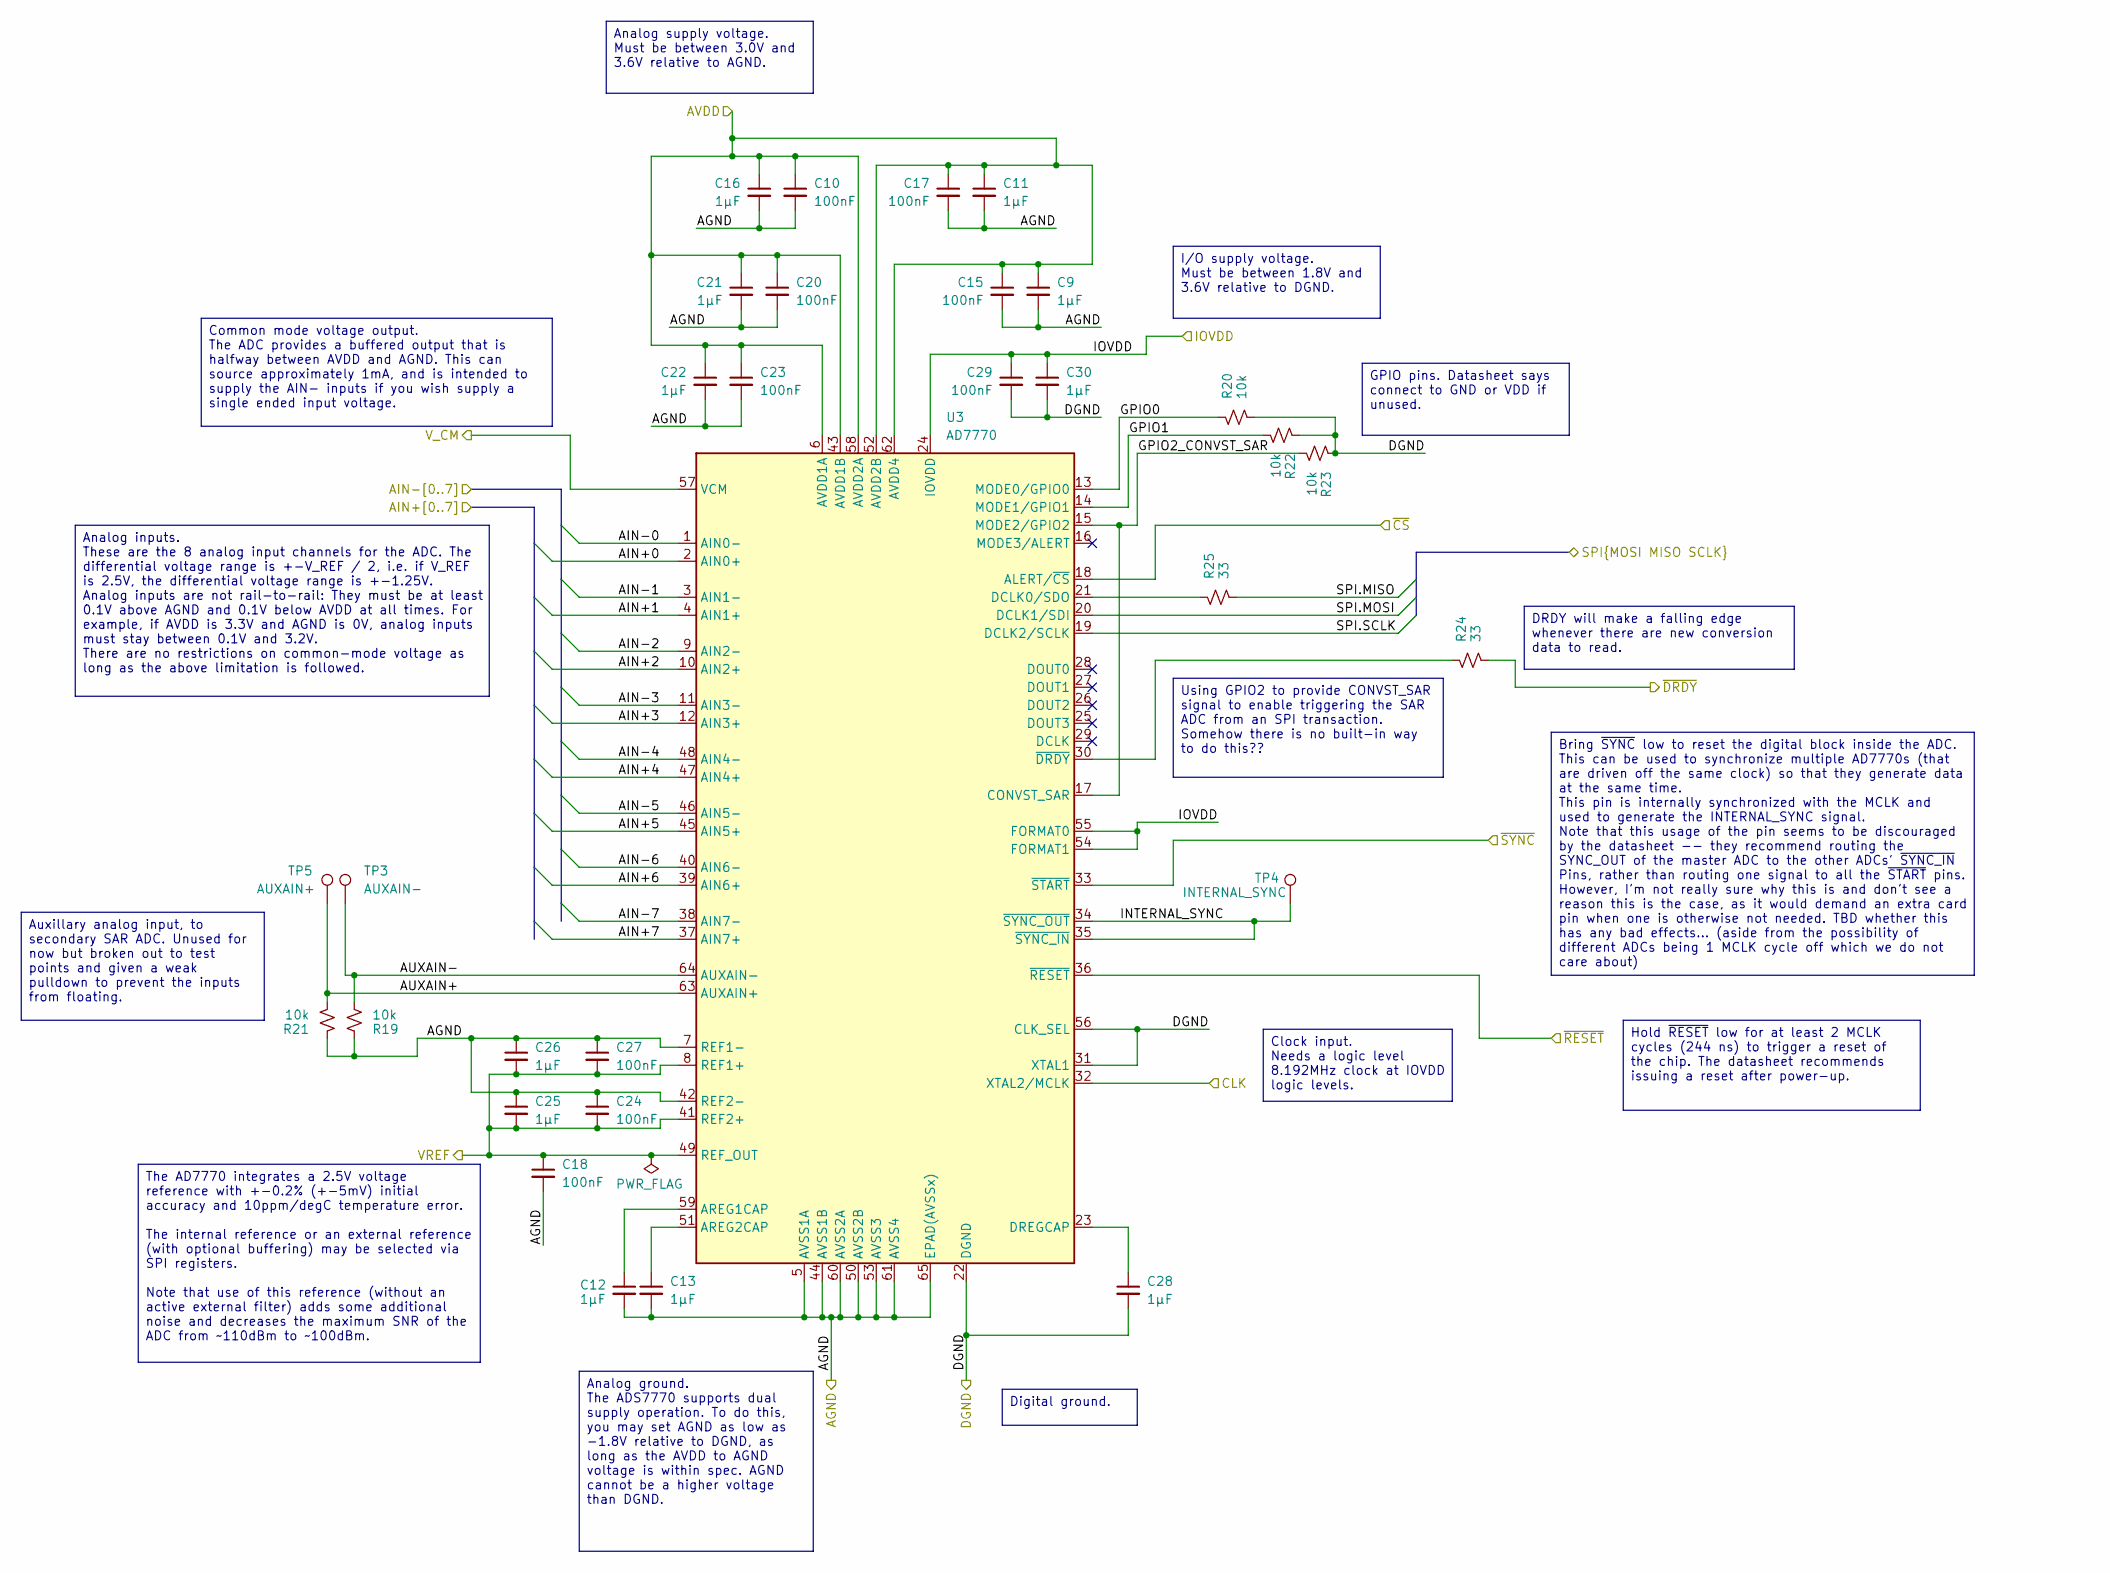
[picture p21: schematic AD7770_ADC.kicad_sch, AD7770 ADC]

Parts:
C9, C11, C12, C13, C16, C21, C22, C25, C26, C28, C30: 1µF; C_0603_1608Metric
C10, C15, C17, C18, C20, C23, C24, C27, C29: 100nF; C_0603_1608Metric
R19, R20, R21, R22, R23: 10k; R_0603_1608Metric
R24, R25: 33; R_0603_1608Metric
TP3: AUXAIN-; TestPoint_THTPad_D2.5mm_Drill1.2mm
TP4: INTERNAL_SYNC; TestPoint_THTPad_D2.5mm_Drill1.2mm
TP5: AUXAIN+; TestPoint_THTPad_D2.5mm_Drill1.2mm
U3: AD7770; LFCSP-64-1EP_9x9mm_P0.5mm_EP5.21x5.21mm_LeadsExtended

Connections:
+2.5V_REF: C18.1, C24.2, C25.2, C26.2, C27.2, U3.8 (REF1+), U3.41 (REF2+), U3.49 (REF_OUT); also elsewhere on the board
+3.3V: C29.1, C30.1, U3.24 (IOVDD), U3.54 (FORMAT1), U3.55 (FORMAT0); also elsewhere on the board
+3.3VA: C9.1, C10.1, C11.1, C15.1, C16.1, C17.1, C20.1, C21.1, C22.1, C23.1, U3.6 (AVDD1A), U3.43 (AVDD1B), U3.52 (AVDD2B), U3.58 (AVDD2A), U3.62 (AVDD4); also elsewhere on the board
/8.192MHZ_CLK: U3.32 (XTAL2/MCLK); also elsewhere on the board
/AD7770 ADC/AIN+0: U3.2 (AIN0+); also elsewhere on the board
/AD7770 ADC/AIN+1: U3.4 (AIN1+); also elsewhere on the board
/AD7770 ADC/AIN+2: U3.10 (AIN2+); also elsewhere on the board
/AD7770 ADC/AIN+3: U3.12 (AIN3+); also elsewhere on the board
/AD7770 ADC/AIN+4: U3.47 (AIN4+); also elsewhere on the board
/AD7770 ADC/AIN+5: U3.45 (AIN5+); also elsewhere on the board
/AD7770 ADC/AIN+6: U3.39 (AIN6+); also elsewhere on the board
/AD7770 ADC/AIN+7: U3.37 (AIN7+); also elsewhere on the board
/AD7770 ADC/AIN-0: U3.1 (AIN0-); also elsewhere on the board
/AD7770 ADC/AIN-1: U3.3 (AIN1-); also elsewhere on the board
/AD7770 ADC/AIN-2: U3.9 (AIN2-); also elsewhere on the board
/AD7770 ADC/AIN-3: U3.11 (AIN3-); also elsewhere on the board
/AD7770 ADC/AIN-4: U3.48 (AIN4-); also elsewhere on the board
/AD7770 ADC/AIN-5: U3.46 (AIN5-); also elsewhere on the board
/AD7770 ADC/AIN-6: U3.40 (AIN6-); also elsewhere on the board
/AD7770 ADC/AIN-7: U3.38 (AIN7-); also elsewhere on the board
/AD7770 ADC/AUXAIN+: R21.2, TP5.1, U3.63 (AUXAIN+)
/AD7770 ADC/AUXAIN-: R19.2, TP3.1, U3.64 (AUXAIN-)
/AD7770 ADC/GPIO0: R20.1, U3.13 (MODE0/GPIO0)
/AD7770 ADC/GPIO1: R22.2, U3.14 (MODE1/GPIO1)
/AD7770 ADC/GPIO2_CONVST_SAR: R23.2, U3.15 (MODE2/GPIO2), U3.17 (CONVST_SAR)
/AD7770 ADC/INTERNAL_SYNC: TP4.1, U3.34 (~SYNC_OUT), U3.35 (~SYNC_IN)
/AD7770 ADC/SPI.MISO: R25.2; also elsewhere on the board
/AD7770 ADC/SPI.MOSI: U3.20 (DCLK1/SDI); also elsewhere on the board
/AD7770 ADC/SPI.SCLK: U3.19 (DCLK2/SCLK); also elsewhere on the board
/AD7770 ADC/V_CM: U3.57 (VCM); also elsewhere on the board
/AD7770 ADC/~DRDY: R24.2; also elsewhere on the board
/AD7770 ADC/~RESET: U3.36 (~RESET); also elsewhere on the board
/AD7770 ADC/~SYNC: U3.33 (~START); also elsewhere on the board
/B2B Connector Card Side/CS0: U3.18 (ALERT/~CS); also elsewhere on the board
GND: C9.2, C10.2, C11.2, C12.2, C13.2, C15.2, C16.2, C17.2, C18.2, C20.2, C21.2, C22.2, C23.2, C24.1, C25.1, C26.1, C27.1, C28.2, C29.2, C30.2, R19.1, R20.2, R21.1, R22.1, R23.1, U3.5 (AVSS1A), U3.7 (REF1-), U3.22 (DGND), U3.31 (XTAL1), U3.42 (REF2-), U3.44 (AVSS1B), U3.50 (AVSS2B), U3.53 (AVSS3), U3.56 (CLK_SEL), U3.60 (AVSS2A), U3.61 (AVSS4), U3.65 (EPAD(AVSSx)); also elsewhere on the board
unnamed: C12.1, U3.59 (AREG1CAP)
unnamed: C13.1, U3.51 (AREG2CAP)
unnamed: R25.1, U3.21 (DCLK0/SDO)
unnamed: C28.1, U3.23 (DREGCAP)
unnamed: R24.1, U3.30 (~DRDY)

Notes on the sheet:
Analog inputs. These are the 8 analog input channels for the ADC. The differential voltage range is +-V_REF / 2, i.e. if V_REF is 2.5V, the differential voltage range is +-1.25V. Analog inputs are not rail-to-rail: They must be at least 0.1V above AGND and 0.1V below AVDD at all times. For example,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
Digital ground.
GPIO pins. Datasheet says connect to GND or VDD if unused.
Bring ~{SYNC} low to reset the digital block inside the ADC. This can be used to synchronize multiple AD7770s (that are driven off the same clock) so that they generate data at the same time. This pin is internally synchronized with the MCLK and used to generate the INTERNAL_SYNC signal. Note that 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
Auxillary analog input, to secondary SAR ADC. Unused for now but broken out to test points and given a weak pulldown to prevent the inputs from floating.
Using GPIO2 to provide CONVST_SAR signal to enable triggering the SAR ADC from an SPI transaction. Somehow there is no built-in way to do this??
The AD7770 integrates a 2.5V voltage reference with +-0.2% (+-5mV) initial accuracy and 10ppm/degC temperature error. The internal reference or an external reference (with optional buffering) may be selected via SPI registers. Note that use of this reference (without an active external filter) adds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
Clock input. Needs a logic level 8.192MHz clock at IOVDD logic levels.
Analog supply voltage. Must be between 3.0V and 3.6V relative to AGND.
Common mode voltage output. The ADC provides a buffered output that is halfway between AVDD and AGND. This can source approximately 1mA, and is intended to supply the AIN- inputs if you wish supply a single ended input voltage.
DRDY will make a falling edge whenever there are new conversion data to read.
Analog ground. The ADS7770 supports dual supply operation. To do this, you may set AGND as low as -1.8V relative to DGND, as long as the AVDD to AGND voltage is within spec. AGND cannot be a higher voltage than DGND.
I/O supply voltage. Must be between 1.8V and 3.6V relative to DGND.
Hold ~{RESET} low for at least 2 MCLK cycles (244 ns) to trigger a reset of the chip. The datasheet recommends issuing a reset after power-up.

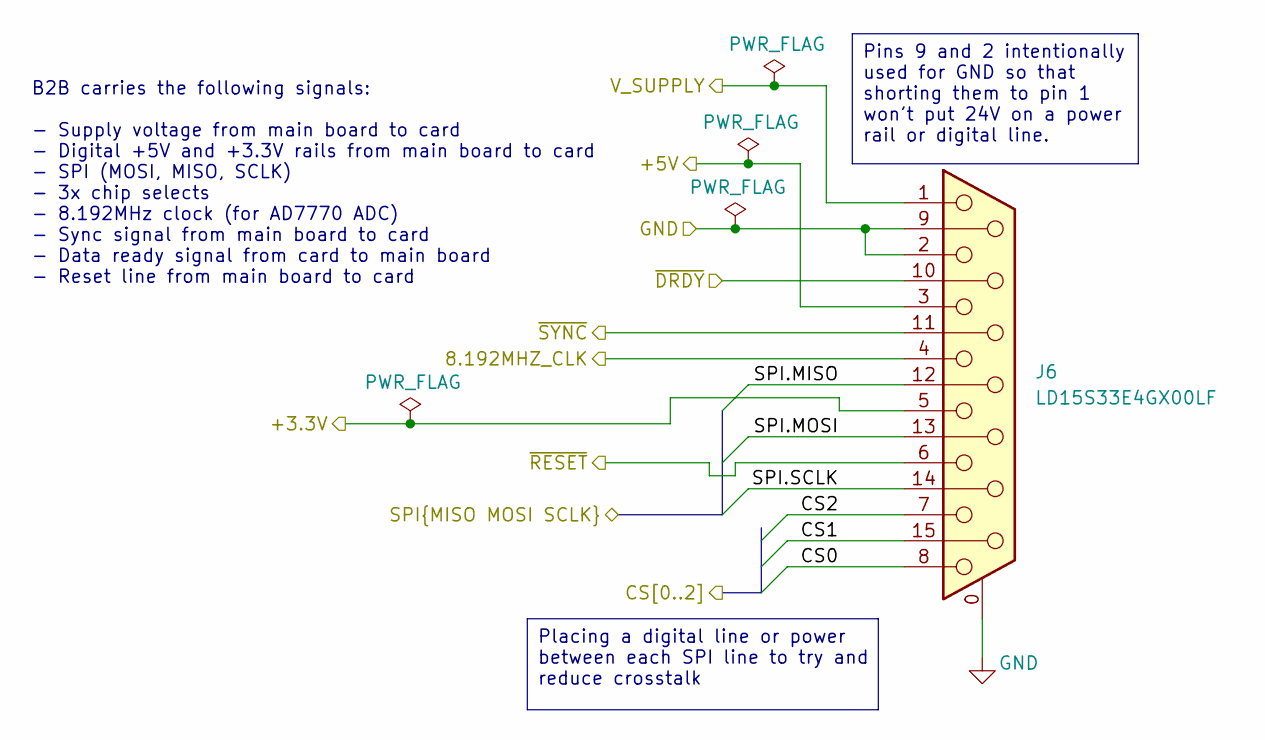
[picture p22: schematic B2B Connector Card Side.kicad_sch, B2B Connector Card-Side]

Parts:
J6: LD15S33E4GX00LF; Amphenol_LD15S33E4GX00LF

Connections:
+3.3V: J6.5; also elsewhere on the board
+5V: J6.3; also elsewhere on the board
+V_SUPPLY: J6.1; also elsewhere on the board
/8.192MHZ_CLK: J6.4; also elsewhere on the board
/AD7770 ADC/SPI.MISO: J6.12; also elsewhere on the board
/AD7770 ADC/SPI.MOSI: J6.13; also elsewhere on the board
/AD7770 ADC/SPI.SCLK: J6.14; also elsewhere on the board
/AD7770 ADC/~DRDY: J6.10; also elsewhere on the board
/AD7770 ADC/~RESET: J6.6; also elsewhere on the board
/AD7770 ADC/~SYNC: J6.11 (P111); also elsewhere on the board
/B2B Connector Card Side/CS0: J6.8; also elsewhere on the board
/B2B Connector Card Side/CS1: J6.15
/B2B Connector Card Side/CS2: J6.7; also elsewhere on the board
GND: J6.0 (PAD), J6.2, J6.9; also elsewhere on the board

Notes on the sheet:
B2B carries the following signals: - Supply voltage from main board to card - Digital +5V and +3.3V rails from main board to card - SPI (MOSI, MISO, SCLK) - 3x chip selects - 8.192MHz clock (for AD7770 ADC) - Sync signal from main board to card - Data ready signal from card to main board - Reset li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
Pins 9 and 2 intentionally used for GND so that shorting them to pin 1 won't put 24V on a power rail or digital line.
Placing a digital line or power between each SPI line to try and reduce crosstalk

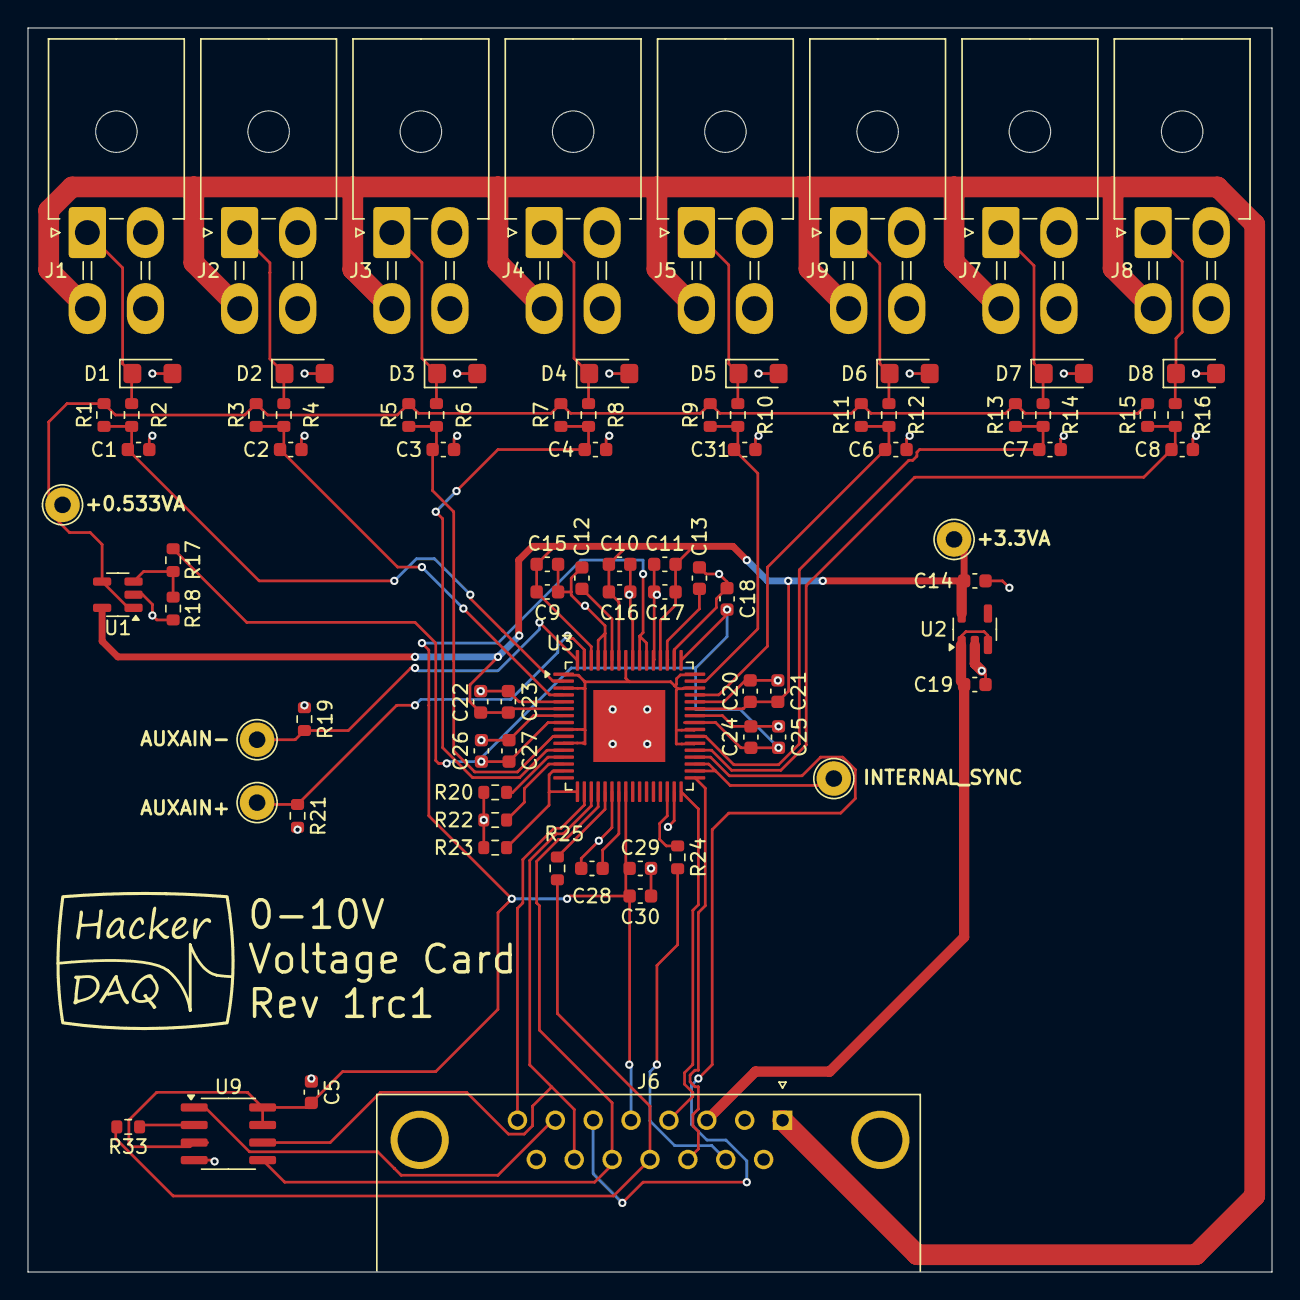
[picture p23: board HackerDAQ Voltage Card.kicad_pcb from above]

Board: 2 copper layers, 90.0 x 90.0 mm, 92 parts (0 on the bottom side), 54 nets.

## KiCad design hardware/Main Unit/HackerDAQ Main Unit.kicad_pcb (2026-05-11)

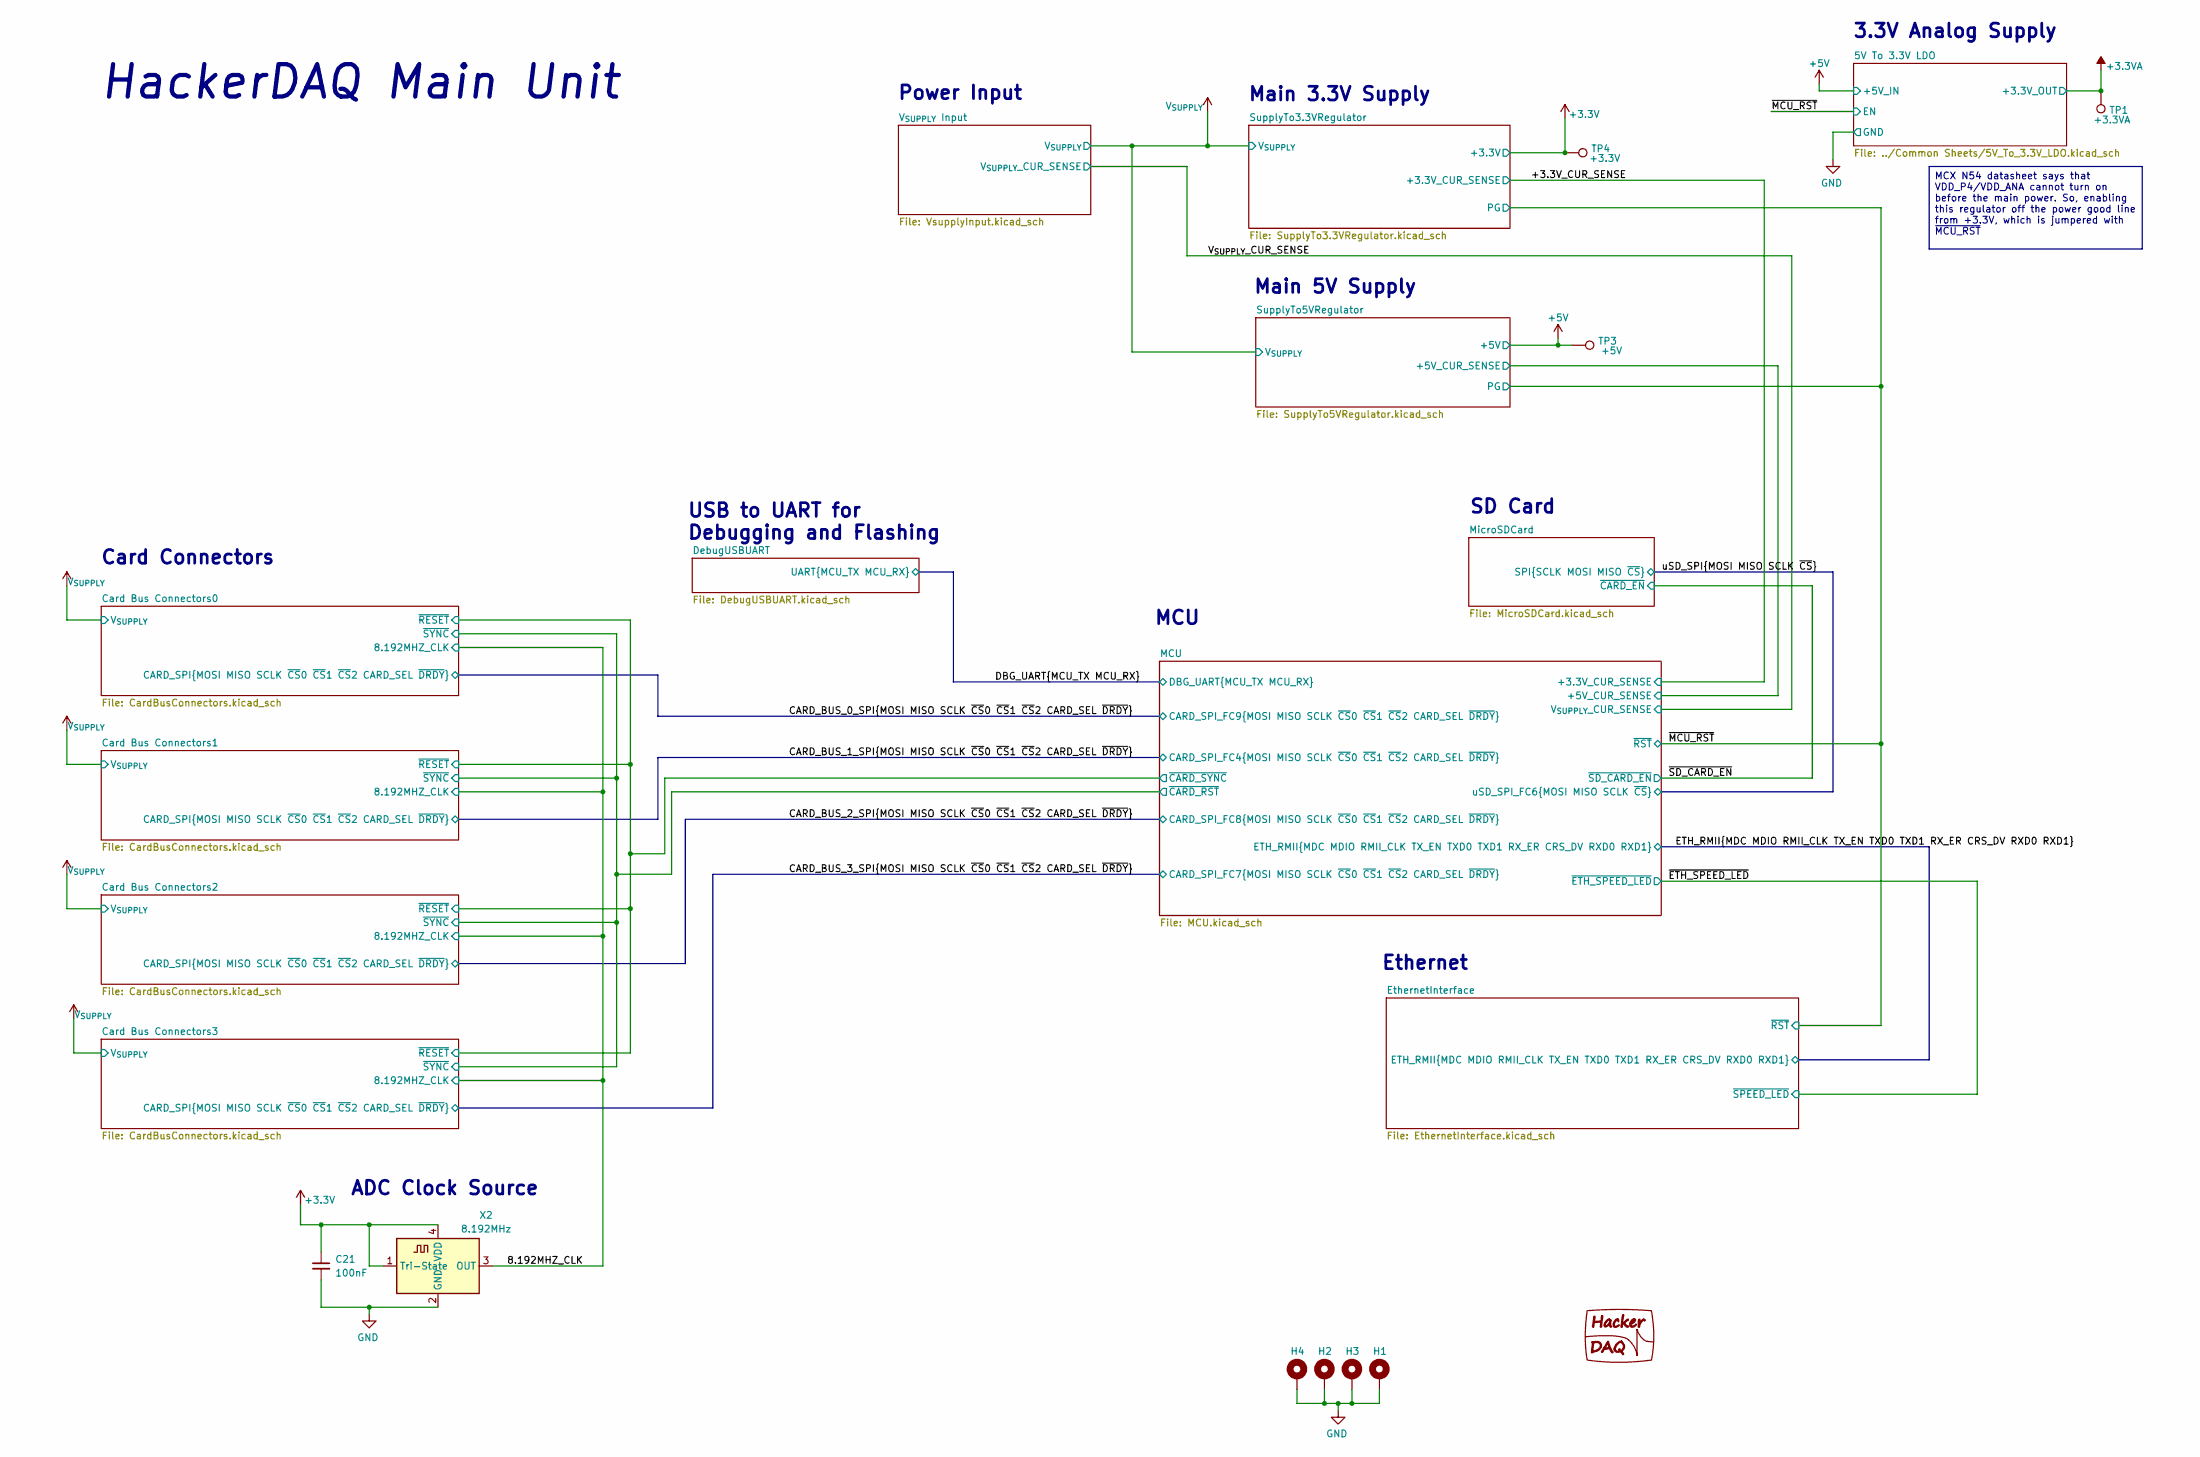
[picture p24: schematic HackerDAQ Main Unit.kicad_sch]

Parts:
C21: 100nF; C_0603_1608Metric
H1, H2, H3, H4: MountingHole_Pad; MountingHole_4.3mm_M4_DIN965_Pad
LG1: HackerDAQ Logo
TP1: +3.3VA; TestPoint_THTPad_D2.5mm_Drill1.2mm
TP3: +5V; TestPoint_THTPad_D2.5mm_Drill1.2mm
TP4: +3.3V; TestPoint_THTPad_D2.5mm_Drill1.2mm
X2: 8.192MHz; Oscillator_SMD_ECS_2520MV-xxx-xx-4Pin_2.5x2.0mm_Fixed3DModel

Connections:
/8.192MHZ_CLK: X2.3 (OUT); also elsewhere on the board
GND: C21.2, H1.1, H2.1, H3.1, H4.1, X2.2 (GND); also elsewhere on the board

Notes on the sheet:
ADC Clock Source
HackerDAQ Main Unit
Main 3.3V Supply
MCU
Ethernet
Card Connectors
SD Card
USB to UART for Debugging and Flashing
3.3V Analog Supply
Main 5V Supply
Power Input
MCX N54 datasheet says that VDD_P4/VDD_ANA cannot turn on before the main power. So, enabling this regulator off the power good line from +3.3V, which is jumpered with ~{MCU_RST}

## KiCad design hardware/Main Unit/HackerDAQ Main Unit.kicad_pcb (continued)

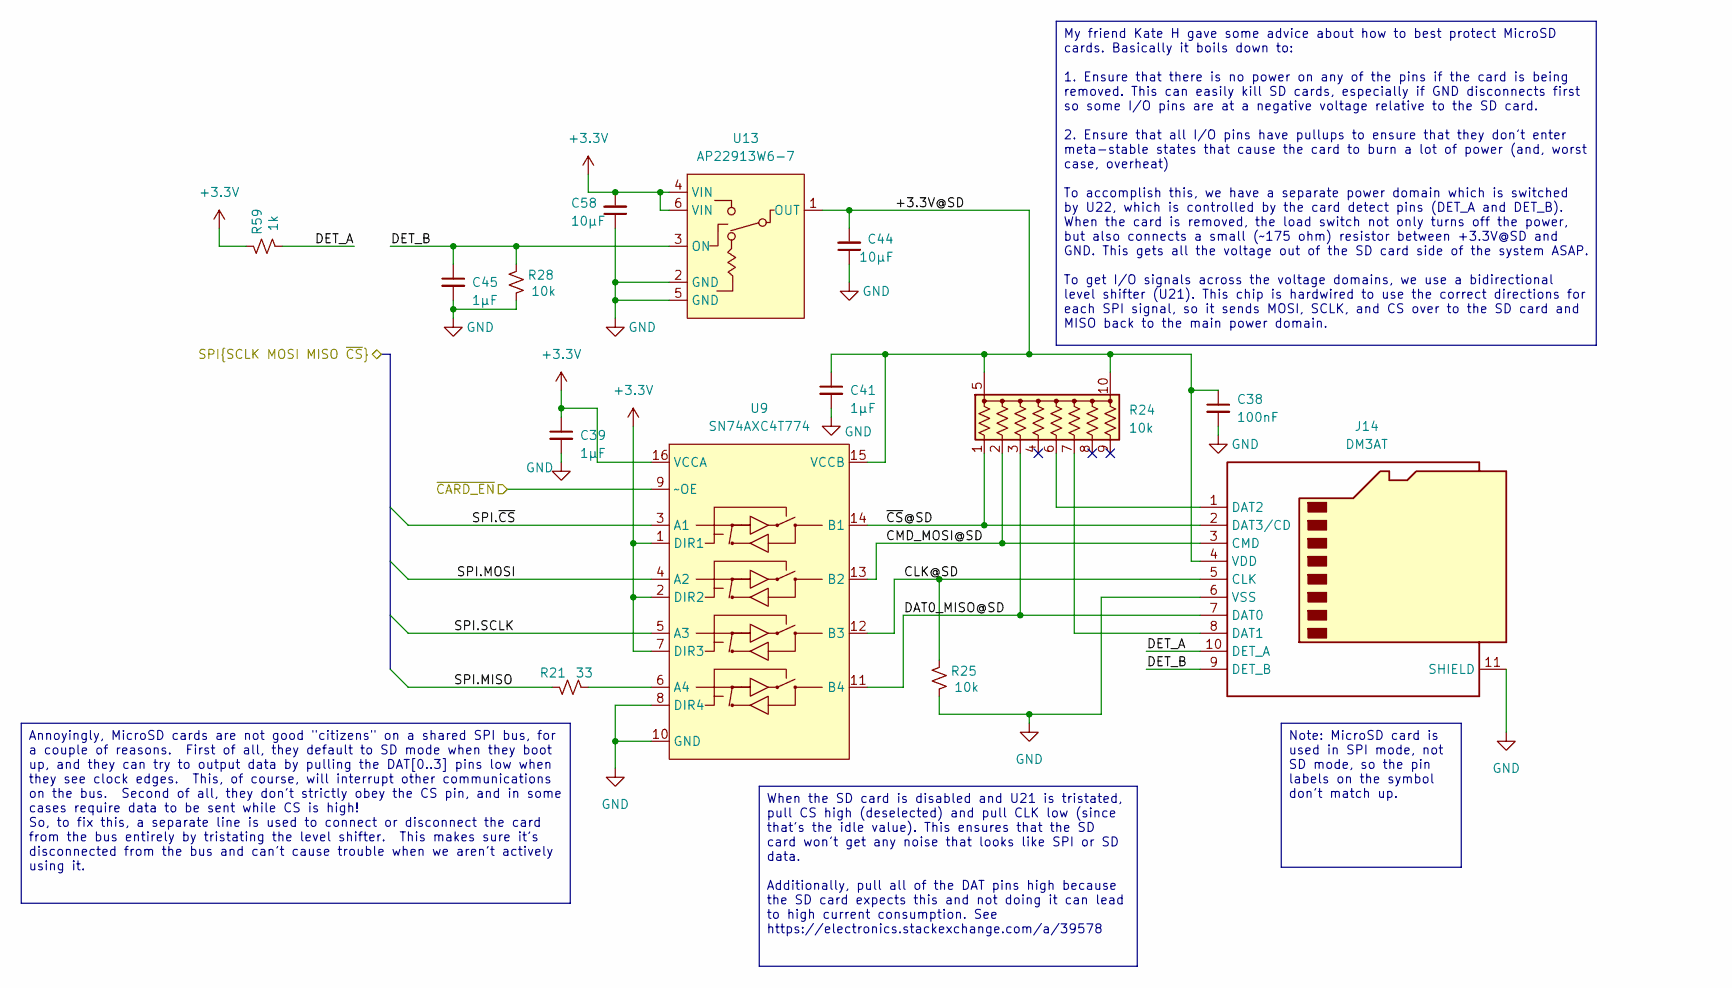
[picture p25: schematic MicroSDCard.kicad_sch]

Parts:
C38: 100nF; C_0603_1608Metric
C39, C41, C45: 1µF; C_0603_1608Metric
C44, C58: 10µF; C_1206_3216Metric
J14: DM3AT; microSD_HC_Hirose_DM3AT-SF-PEJM5
R21: 33; R_0603_1608Metric
R24: 10k; CTS 745C101
R25, R28: 10k; R_0603_1608Metric
R59: 1k; R_0603_1608Metric
U9: SN74AXC4T774; TSSOP-16_4.4x5mm_P0.65mm
U13: AP22913W6-7; SOT-23-6

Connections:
/MicroSDCard/+3.3V@SD: C38.1, C41.1, C44.2, J14.4 (VDD), R24.5 (common), R24.10 (common), U9.15 (VCCB), U13.1 (OUT)
/MicroSDCard/CLK@SD: J14.5 (CLK), R25.2, U9.12 (B3)
/MicroSDCard/CMD_MOSI@SD: J14.3 (CMD), R24.2 (R2), U9.13 (B2)
/MicroSDCard/DAT0_MISO@SD: J14.7 (DAT0), R24.3 (R3), U9.11 (B4)
/MicroSDCard/DET_A: J14.10 (DET_A), R59.1
/MicroSDCard/DET_B: C45.1, J14.9 (DET_B), R28.2, U13.3 (ON)
/MicroSDCard/~CS@SD: J14.2 (DAT3/CD), R24.1 (R1), U9.14 (B1)
/uSD_SPI.MISO: R21.1; also elsewhere on the board
/uSD_SPI.MOSI: U9.4 (A2); also elsewhere on the board
/uSD_SPI.SCLK: U9.5 (A3); also elsewhere on the board
/uSD_SPI.~CS: U9.3 (A1); also elsewhere on the board
/~SD_CARD_EN: U9.9 (~OE); also elsewhere on the board
GND: C38.2, C39.2, C41.2, C44.1, C45.2, C58.1, J14.6 (VSS), J14.11 (SHIELD), R25.1, R28.1, U9.8 (DIR4), U9.10 (GND), U13.2 (GND), U13.5 (GND); also elsewhere on the board
unnamed: J14.8 (DAT1), R24.7 (R6)
unnamed: J14.1 (DAT2), R24.6 (R5)
unnamed: R21.2, U9.6 (A4)

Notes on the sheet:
Note: MicroSD card is used in SPI mode, not SD mode, so the pin labels on the symbol don't match up.
When the SD card is disabled and U21 is tristated, pull CS high (deselected) and pull CLK low (since that's the idle value). This ensures that the SD card won't get any noise that looks like SPI or SD data. Additionally, pull all of the DAT pins high because the SD card expects this and not doing i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
My friend Kate H gave some advice about how to best protect MicroSD cards. Basically it boils down to: 1. Ensure that there is no power on any of the pins if the card is being removed. This can easily kill SD cards, especially if GND disconnects first so some I/O pins are at a negative voltage rela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
Annoyingly, MicroSD cards are not good "citizens" on a shared SPI bus, for a couple of reasons. First of all, they default to SD mode when they boot up, and they can try to output data by pulling the DAT[0..3] pins low when they see clock edges. This, of course, will interrupt other communications 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

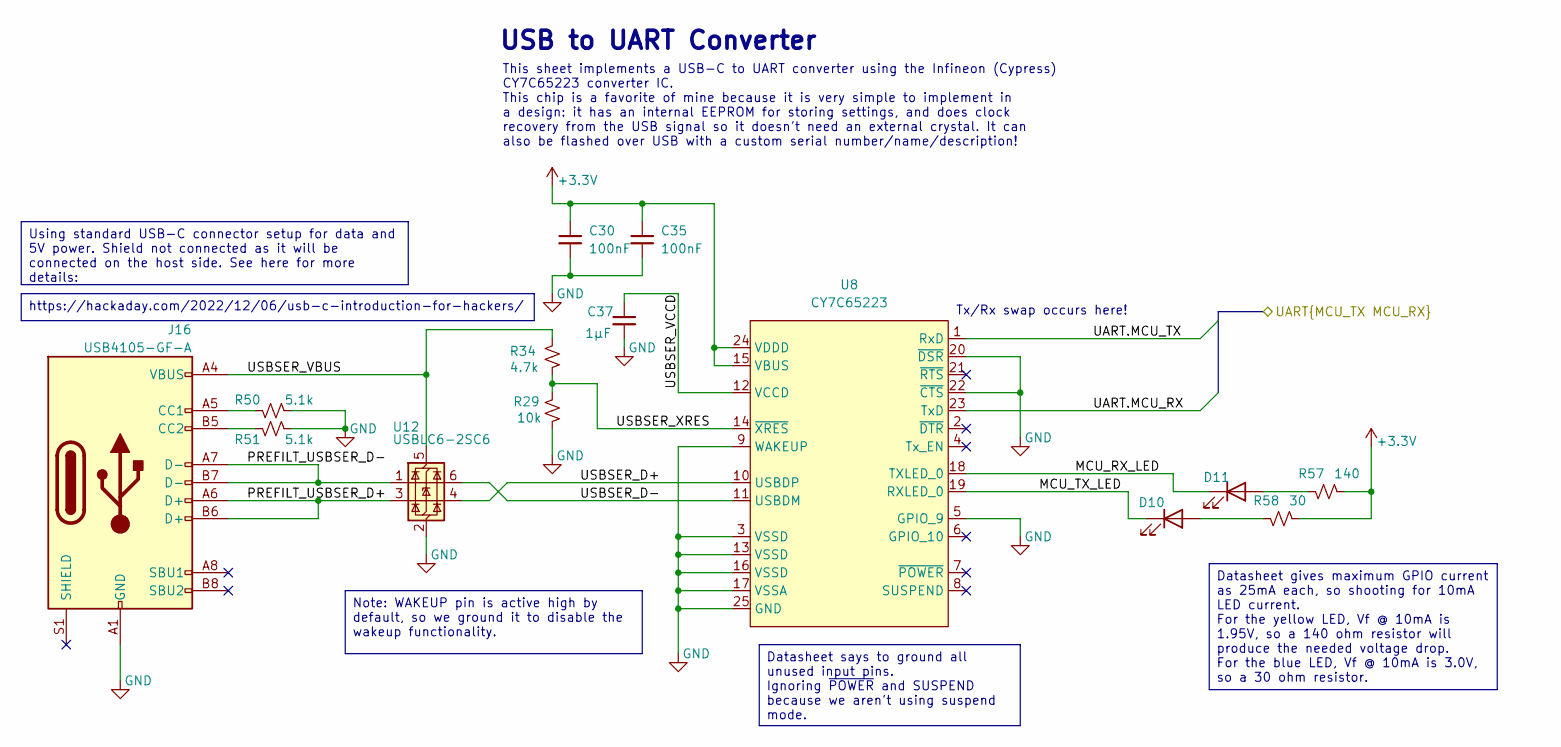
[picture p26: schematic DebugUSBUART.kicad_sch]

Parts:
C30, C35: 100nF; C_0603_1608Metric
C37: 1µF; C_0603_1608Metric
D10: AA3528QBS; AA3528
D11: AA3528SYSK; AA3528
J16: USB4105-GF-A; USB_C_Receptacle_GCT_USB4105-xx-A_16P_TopMnt_Horizontal-Ext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
R29: 10k; R_0603_1608Metric
R34: 4.7k; R_0603_1608Metric
R50, R51: 5.1k; R_0603_1608Metric
R57: 140; R_0603_1608Metric
R58: 30; R_0603_1608Metric
U8: CY7C65223; QFN-24-1EP_4x4mm_P0.5mm_EP2.65x2.65mm-LengthenedPads
U12: USBLC6-2SC6; SOT-23-6

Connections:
/DBG_UART.MCU_RX: U8.23 (TxD); also elsewhere on the board
/DBG_UART.MCU_TX: U8.1 (RxD); also elsewhere on the board
/DebugUSBUART/MCU_RX_LED: D11.1 (K), U8.18 (TXLED_0)
/DebugUSBUART/MCU_TX_LED: D10.1 (K), U8.19 (RXLED_0)
/DebugUSBUART/PREFILT_USBSER_D+: J16.A6 (D+), J16.B6 (D+), U12.3 (I/O2)
/DebugUSBUART/PREFILT_USBSER_D-: J16.A7 (D-), J16.B7 (D-), U12.1 (I/O1)
/DebugUSBUART/USBSER_D+: U8.10 (USBDP), U12.4 (I/O2)
/DebugUSBUART/USBSER_D-: U8.11 (USBDM), U12.6 (I/O1)
/DebugUSBUART/USBSER_VBUS: J16.A4 (VBUS), J16.A9 (VBUS), J16.B4 (VBUS), J16.B9 (VBUS), R34.2, U12.5 (VBUS)
/DebugUSBUART/USBSER_VCCD: C37.1, U8.12 (VCCD)
/DebugUSBUART/USBSER_XRES: R29.2, R34.1, U8.14 (~XRES)
GND: C30.2, C35.2, C37.2, J16.A1 (GND), J16.A12 (GND), J16.B1 (GND), J16.B12 (GND), R29.1, R50.1, R51.1, U8.3 (VSSD), U8.5 (GPIO_9), U8.9 (WAKEUP), U8.13 (VSSD), U8.16 (VSSD), U8.17 (VSSA), U8.20 (~DSR), U8.22 (~CTS), U8.25 (GND), U12.2 (GND); also elsewhere on the board
unnamed: D10.2 (A), R58.2
unnamed: D11.2 (A), R57.2
unnamed: J16.A5 (CC1), R50.2
unnamed: J16.B5 (CC2), R51.2

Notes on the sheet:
This sheet implements a USB-C to UART converter using the Infineon (Cypress) CY7C65223 converter IC. This chip is a favorite of mine because it is very simple to implement in a design: it has an internal EEPROM for storing settings, and does clock recovery from the USB signal so it doesn't need an 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
USB to UART Converter
Tx/Rx swap occurs here!
Datasheet says to ground all unused input pins. Ignoring ~{POWER} and SUSPEND because we aren't using suspend mode.
https://hackaday.com/2022/12/06/usb-c-introduction-for-hackers/
Datasheet gives maximum GPIO current as 25mA each, so shooting for 10mA LED current. For the yellow LED, Vf @ 10mA is 1.95V, so a 140 ohm resistor will produce the needed voltage drop. For the blue LED, Vf @ 10mA is 3.0V, so a 30 ohm resistor.
Note: WAKEUP pin is active high by default, so we ground it to disable the wakeup functionality.
Using standard USB-C connector setup for data and 5V power. Shield not connected as it will be connected on the host side. See here for more details:

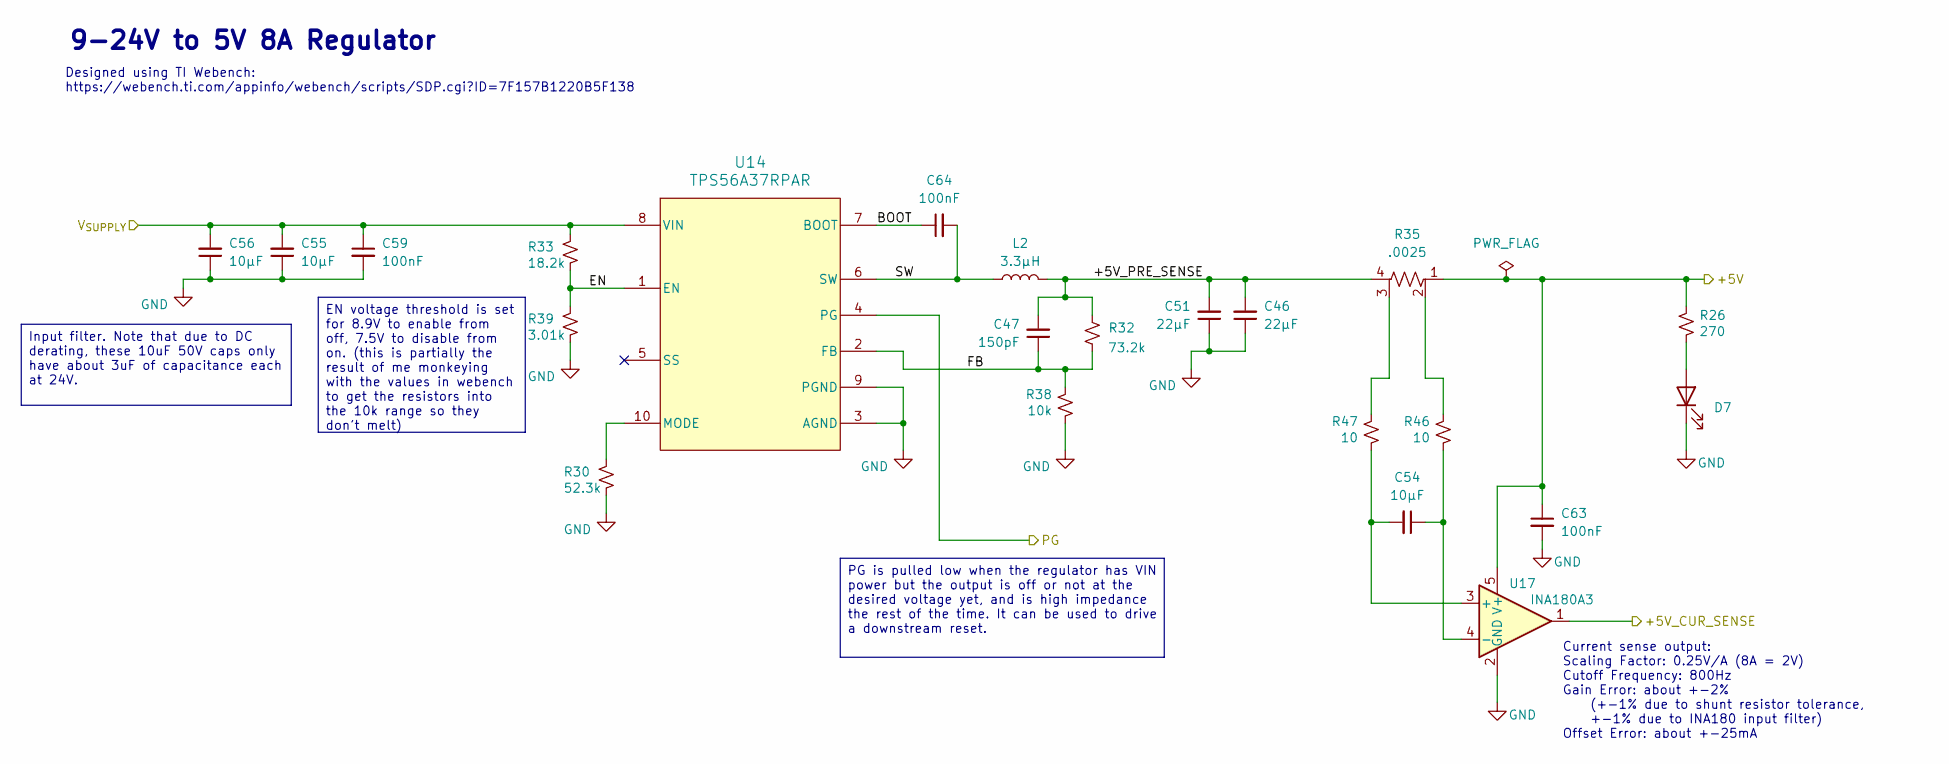
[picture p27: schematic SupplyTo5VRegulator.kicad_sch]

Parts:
C46, C51: 22µF; C_1210_3225Metric
C47: 150pF; C_0603_1608Metric
C54: 10µF; C_1206_3216Metric
C55, C56: 10µF; C_1210_3225Metric
C59, C63, C64: 100nF; C_0603_1608Metric
D7: AA3528CGSK; AA3528
L2: 3.3μH; L_Vishay_IHLP-3232
R26: 270; R_0603_1608Metric
R30: 52.3k; R_0603_1608Metric
R32: 73.2k; R_0603_1608Metric
R33: 18.2k; R_0603_1608Metric
R35: .0025; D1FCP0612
R38: 10k; R_0603_1608Metric
R39: 3.01k; R_0603_1608Metric
R46, R47: 10; R_0603_1608Metric
U14: TPS56A37RPAR; RPA0010A-MFG
U17: INA180A3; SOT-23-5

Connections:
/MCU/+5V_CUR_SENSE: U17.1; also elsewhere on the board
/SupplyTo5VRegulator/+5V_PRE_SENSE: C46.2, C47.2, C51.2, L2.2, R32.2, R35.4
/SupplyTo5VRegulator/BOOT: C64.1, U14.7 (BOOT)
/SupplyTo5VRegulator/EN: R33.1, R39.2, U14.1 (EN)
/SupplyTo5VRegulator/FB: C47.1, R32.1, R38.1, U14.2 (FB)
/SupplyTo5VRegulator/SW: C64.2, L2.1, U14.6 (SW)
/~MCU_RST: U14.4 (PG); also elsewhere on the board
GND: C46.1, C51.1, C55.1, C56.1, C59.2, C63.2, D7.1 (K), R30.1, R38.2, R39.1, U14.3 (AGND), U14.9 (PGND), U17.2 (GND); also elsewhere on the board
unnamed: D7.2 (A), R26.1
unnamed: R35.2, R46.1
unnamed: R35.3, R47.1
unnamed: R30.2, U14.10 (MODE)
unnamed: C54.2, R47.2, U17.3 (+)
unnamed: C54.1, R46.2, U17.4 (-)
V_{SUPPLY}: C55.2, C56.2, C59.1, R33.2, U14.8 (VIN); also elsewhere on the board

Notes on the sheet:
Designed using TI Webench: https://webench.ti.com/appinfo/webench/scripts/SDP.cgi?ID=7F157B1220B5F138
9-24V to 5V 8A Regulator
Current sense output: Scaling Factor: 0.25V/A (8A = 2V) Cutoff Frequency: 800Hz Gain Error: about +-2% (+-1% due to shunt resistor tolerance, +-1% due to INA180 input filter) Offset Error: about +-25mA
EN voltage threshold is set for 8.9V to enable from off, 7.5V to disable from on. (this is partially the result of me monkeying with the values in webench to get the resistors into the 10k range so they don't melt)
Input filter. Note that due to DC derating, these 10uF 50V caps only have about 3uF of capacitance each at 24V.
PG is pulled low when the regulator has VIN power but the output is off or not at the desired voltage yet, and is high impedance the rest of the time. It can be used to drive a downstream reset.

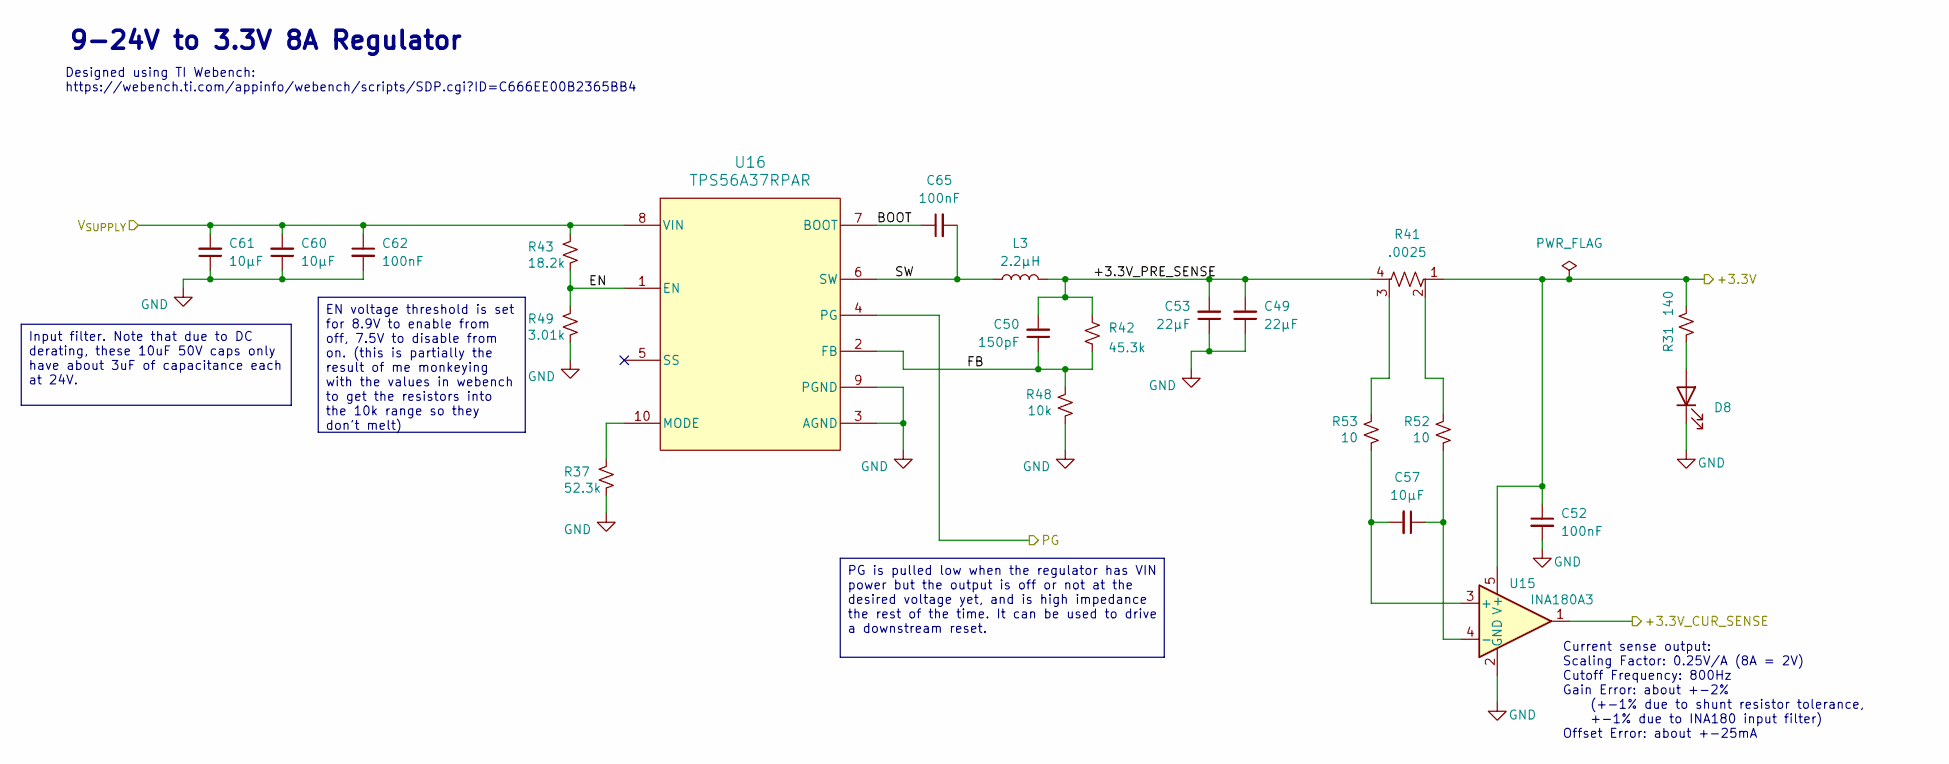
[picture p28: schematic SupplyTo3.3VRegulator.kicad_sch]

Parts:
C49, C53: 22µF; C_1210_3225Metric
C50: 150pF; C_0603_1608Metric
C52, C62, C65: 100nF; C_0603_1608Metric
C57: 10µF; C_1206_3216Metric
C60, C61: 10µF; C_1210_3225Metric
D8: AA3528CGSK; AA3528
L3: 2.2μH; 0630CDMCDDS
R31: 140; R_0603_1608Metric
R37: 52.3k; R_0603_1608Metric
R41: .0025; D1FCP0612
R42: 45.3k; R_0603_1608Metric
R43: 18.2k; R_0603_1608Metric
R48: 10k; R_0603_1608Metric
R49: 3.01k; R_0603_1608Metric
R52, R53: 10; R_0603_1608Metric
U15: INA180A3; SOT-23-5
U16: TPS56A37RPAR; RPA0010A-MFG

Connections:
/+3.3V_CUR_SENSE: U15.1; also elsewhere on the board
/SupplyTo3.3VRegulator/+3.3V_PRE_SENSE: C49.2, C50.2, C53.2, L3.2, R41.4, R42.2
/SupplyTo3.3VRegulator/BOOT: C65.1, U16.7 (BOOT)
/SupplyTo3.3VRegulator/EN: R43.1, R49.2, U16.1 (EN)
/SupplyTo3.3VRegulator/FB: C50.1, R42.1, R48.1, U16.2 (FB)
/SupplyTo3.3VRegulator/SW: C65.2, L3.1, U16.6 (SW)
/~MCU_RST: U16.4 (PG); also elsewhere on the board
GND: C49.1, C52.2, C53.1, C60.1, C61.1, C62.2, D8.1 (K), R37.1, R48.2, R49.1, U15.2 (GND), U16.3 (AGND), U16.9 (PGND); also elsewhere on the board
unnamed: D8.2 (A), R31.2
unnamed: R41.2, R52.1
unnamed: R41.3, R53.1
unnamed: C57.2, R53.2, U15.3 (+)
unnamed: C57.1, R52.2, U15.4 (-)
unnamed: R37.2, U16.10 (MODE)
V_{SUPPLY}: C60.2, C61.2, C62.1, R43.2, U16.8 (VIN); also elsewhere on the board

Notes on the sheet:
Designed using TI Webench: https://webench.ti.com/appinfo/webench/scripts/SDP.cgi?ID=C666EE00B2365BB4
Current sense output: Scaling Factor: 0.25V/A (8A = 2V) Cutoff Frequency: 800Hz Gain Error: about +-2% (+-1% due to shunt resistor tolerance, +-1% due to INA180 input filter) Offset Error: about +-25mA
9-24V to 3.3V 8A Regulator
PG is pulled low when the regulator has VIN power but the output is off or not at the desired voltage yet, and is high impedance the rest of the time. It can be used to drive a downstream reset.
EN voltage threshold is set for 8.9V to enable from off, 7.5V to disable from on. (this is partially the result of me monkeying with the values in webench to get the resistors into the 10k range so they don't melt)
Input filter. Note that due to DC derating, these 10uF 50V caps only have about 3uF of capacitance each at 24V.


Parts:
C36: 100nF; C_0603_1608Metric
J6, J7: 61801525123; Wurth_61801525123
R12: 10k; CTS 745C101
U6: SN74CB3Q3257PWR; TSSOP-16_4.4x5mm_P0.65mm

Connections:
/8.192MHZ_CLK: J6.4, J7.4; also elsewhere on the board
/CARD_BUS_1_SPI.CARD_SEL: U6.1 (S); also elsewhere on the board
/CARD_BUS_1_SPI.MISO: J6.12, J7.12; also elsewhere on the board
/CARD_BUS_1_SPI.MOSI: J6.13, J7.13; also elsewhere on the board
/CARD_BUS_1_SPI.SCLK: J6.14, J7.14; also elsewhere on the board
/CARD_BUS_1_SPI.~CS0: U6.4 (1A); also elsewhere on the board
/CARD_BUS_1_SPI.~CS1: U6.7 (2A); also elsewhere on the board
/CARD_BUS_1_SPI.~CS2: U6.9 (3A); also elsewhere on the board
/CARD_BUS_1_SPI.~DRDY: J6.10, J7.10; also elsewhere on the board
/Card Bus Connectors0/~RESET: J6.6, J7.6; also elsewhere on the board
/Card Bus Connectors0/~SYNC: J6.11 (P111), J7.11 (P111); also elsewhere on the board
/Card Bus Connectors1/F_CARD_CS.~CS0: J6.8, R12.2 (R2), U6.3 (1B2)
/Card Bus Connectors1/F_CARD_CS.~CS1: J6.15, R12.3 (R3), U6.6 (2B2)
/Card Bus Connectors1/F_CARD_CS.~CS2: J6.7, R12.4 (R4), U6.10 (3B2)
/Card Bus Connectors1/L_CARD_CS.~CS0: J7.8, R12.8 (R7), U6.2 (1B1)
/Card Bus Connectors1/L_CARD_CS.~CS1: J7.15, R12.7 (R6), U6.5 (2B1)
/Card Bus Connectors1/L_CARD_CS.~CS2: J7.7, R12.6 (R5), U6.11 (3B1)
GND: C36.2, J6.0 (PAD), J6.2, J6.9, J7.0 (PAD), J7.2, J7.9, U6.8 (GND), U6.12 (4A), U6.15 (~OE); also elsewhere on the board
V_{SUPPLY}: J6.1, J7.1; also elsewhere on the board

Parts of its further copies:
C1, C2, C28: 100nF; C_0603_1608Metric
J2, J3, J4, J5, J8, J9: 61801525123; Wurth_61801525123
R10, R11, R13: 10k; CTS 745C101
U1, U3, U7: SN74CB3Q3257PWR; TSSOP-16_4.4x5mm_P0.65mm

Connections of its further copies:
/8.192MHZ_CLK: J2.4, J3.4, J4.4, J5.4, J8.4, J9.4; also elsewhere on the board
/CARD_BUS_0_SPI.CARD_SEL: U3.1 (S); also elsewhere on the board
/CARD_BUS_0_SPI.MISO: J8.12, J9.12; also elsewhere on the board
/CARD_BUS_0_SPI.MOSI: J8.13, J9.13; also elsewhere on the board
/CARD_BUS_0_SPI.SCLK: J8.14, J9.14; also elsewhere on the board
/CARD_BUS_0_SPI.~CS0: U3.4 (1A); also elsewhere on the board
/CARD_BUS_0_SPI.~CS1: U3.7 (2A); also elsewhere on the board
/CARD_BUS_0_SPI.~CS2: U3.9 (3A); also elsewhere on the board
/CARD_BUS_0_SPI.~DRDY: J8.10, J9.10; also elsewhere on the board
/CARD_BUS_2_SPI.CARD_SEL: U1.1 (S); also elsewhere on the board
/CARD_BUS_2_SPI.MISO: J4.12, J5.12; also elsewhere on the board
/CARD_BUS_2_SPI.MOSI: J4.13, J5.13; also elsewhere on the board
/CARD_BUS_2_SPI.SCLK: J4.14, J5.14; also elsewhere on the board
/CARD_BUS_2_SPI.~CS0: U1.4 (1A); also elsewhere on the board
/CARD_BUS_2_SPI.~CS1: U1.7 (2A); also elsewhere on the board
/CARD_BUS_2_SPI.~CS2: U1.9 (3A); also elsewhere on the board
/CARD_BUS_2_SPI.~DRDY: J4.10, J5.10; also elsewhere on the board
/CARD_BUS_3_SPI.CARD_SEL: U7.1 (S); also elsewhere on the board
/CARD_BUS_3_SPI.MISO: J2.12, J3.12; also elsewhere on the board
/CARD_BUS_3_SPI.MOSI: J2.13, J3.13; also elsewhere on the board
/CARD_BUS_3_SPI.SCLK: J2.14, J3.14; also elsewhere on the board
/CARD_BUS_3_SPI.~CS0: U7.4 (1A); also elsewhere on the board
/CARD_BUS_3_SPI.~CS1: U7.7 (2A); also elsewhere on the board
/CARD_BUS_3_SPI.~CS2: U7.9 (3A); also elsewhere on the board
/CARD_BUS_3_SPI.~DRDY: J2.10, J3.10; also elsewhere on the board
/Card Bus Connectors0/F_CARD_CS.~CS0: J8.8, R10.2 (R2), U3.3 (1B2)
/Card Bus Connectors0/F_CARD_CS.~CS1: J8.15, R10.3 (R3), U3.6 (2B2)
/Card Bus Connectors0/F_CARD_CS.~CS2: J8.7, R10.4 (R4), U3.10 (3B2)
/Card Bus Connectors0/L_CARD_CS.~CS0: J9.8, R10.8 (R7), U3.2 (1B1)
/Card Bus Connectors0/L_CARD_CS.~CS1: J9.15, R10.7 (R6), U3.5 (2B1)
/Card Bus Connectors0/L_CARD_CS.~CS2: J9.7, R10.6 (R5), U3.11 (3B1)
/Card Bus Connectors0/~RESET: J2.6, J3.6, J4.6, J5.6, J8.6, J9.6; also elsewhere on the board
/Card Bus Connectors0/~SYNC: J2.11 (P111), J3.11 (P111), J4.11 (P111), J5.11 (P111), J8.11 (P111), J9.11 (P111); also elsewhere on the board
/Card Bus Connectors2/F_CARD_CS.~CS0: J4.8, R13.2 (R2), U1.3 (1B2)
/Card Bus Connectors2/F_CARD_CS.~CS1: J4.15, R13.3 (R3), U1.6 (2B2)
/Card Bus Connectors2/F_CARD_CS.~CS2: J4.7, R13.4 (R4), U1.10 (3B2)
/Card Bus Connectors2/L_CARD_CS.~CS0: J5.8, R13.8 (R7), U1.2 (1B1)
/Card Bus Connectors2/L_CARD_CS.~CS1: J5.15, R13.7 (R6), U1.5 (2B1)
/Card Bus Connectors2/L_CARD_CS.~CS2: J5.7, R13.6 (R5), U1.11 (3B1)
/Card Bus Connectors3/F_CARD_CS.~CS0: J2.8, R11.2 (R2), U7.3 (1B2)
/Card Bus Connectors3/F_CARD_CS.~CS1: J2.15, R11.3 (R3), U7.6 (2B2)
/Card Bus Connectors3/F_CARD_CS.~CS2: J2.7, R11.4 (R4), U7.10 (3B2)
/Card Bus Connectors3/L_CARD_CS.~CS0: J3.8, R11.8 (R7), U7.2 (1B1)
/Card Bus Connectors3/L_CARD_CS.~CS1: J3.15, R11.7 (R6), U7.5 (2B1)
/Card Bus Connectors3/L_CARD_CS.~CS2: J3.7, R11.6 (R5), U7.11 (3B1)
GND: C1.2, C2.2, C28.2, J2.0 (PAD), J2.2, J2.9, J3.0 (PAD), J3.2, J3.9, J4.0 (PAD), J4.2, J4.9, J5.0 (PAD), J5.2, J5.9, J8.0 (PAD), J8.2, J8.9, J9.0 (PAD), J9.2, J9.9, U1.8 (GND), U1.12 (4A), U1.15 (~OE), U3.8 (GND), U3.12 (4A), U3.15 (~OE), U7.8 (GND), U7.12 (4A), U7.15 (~OE); also elsewhere on the board
V_{SUPPLY}: J2.1, J3.1, J4.1, J5.1, J8.1, J9.1; also elsewhere on the board

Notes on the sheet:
Leader Card Connector
Follower Card Connector
CS multiplexer allows switching CS lines between the leader and follower card. Note for firmware: Wait at least 100ns between setting CARD_SEL and toggling CS due to propagation time.


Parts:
C40: 100nF; C_0603_1608Metric
C48: 10µF; C_1206_3216Metric
D9: SMF24A; D_SMF
J12: 0039300020; Molex_Mini-Fit_Jr_5569-02A2_2x01_P4.20mm_Horizontal
J13: PJ-063AH; BarrelJack_CUI_PJ-063AH_Horizontal
R27: .0025; D1FCP0612
R36, R40: 10; R_0603_1608Metric
U10: INA180A3; SOT-23-5

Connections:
/V_{SUPPLY} Input/V_{SUPPLY}_IN: D9.1 (A1), J12.2, J13.1, R27.4
/V_{SUPPLY}_CUR_SENSE: U10.1; also elsewhere on the board
GND: C40.2, D9.2 (A2), J12.1, J13.2, U10.2 (GND); also elsewhere on the board
unnamed: R27.2, R36.1
unnamed: R27.3, R40.1
unnamed: C48.2, R40.2, U10.3 (+)
unnamed: C48.1, R36.2, U10.4 (-)
V_{SUPPLY}: C40.1, R27.1, U10.5 (V+); also elsewhere on the board

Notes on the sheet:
Current sense output: Scaling Factor: 0.25V/A (8A = 2V) Cutoff Frequency: 800Hz Gain Error: about +-2% (+-1% due to shunt resistor tolerance, +-1% due to INA180 input filter) Offset Error: about +-25mA
Approx power budget: Assume the following usages: - 3.3V regulator: 8A @ 3.3V at 90% efficiency: 29.33W - 5V regulator: 8A @ 5V at 90% efficiency: 44.44W - Each card: 100mA on V_{SUPPLY} This gives that Vsupply must be able to supply about 74W + 800mA, or about 4A @V_{SUPPLY}=24V or about 9A @ V_{S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
Power may be connected via barrel jack (more standard, works with COTS power supplies) or via Mini-Fit connector (more mechanically robust, same connector series as used on the cards)


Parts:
C14: 1µF; C_0603_1608Metric
C19: 100nF; C_0603_1608Metric
U2: TLV71333PDBV; SOT-23-5

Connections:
/~MCU_RST: U2.3 (EN); also elsewhere on the board
GND: C14.2, C19.2, U2.2 (GND); also elsewhere on the board

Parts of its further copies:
C3: 1µF; C_0603_1608Metric
C4: 100nF; C_0603_1608Metric

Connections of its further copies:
GND: C3.2, C4.2; also elsewhere on the board

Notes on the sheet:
Maximum current: 150mA Maximum input voltage: 5.5V
Bring EN above 0.9V to enable the regulator. May jumper to +5V_IN.
Datasheet recommends using at least 0.1uF input and output capacitors. Figure 9 seems to recommend a 1uF output cap for best PSRR performance.

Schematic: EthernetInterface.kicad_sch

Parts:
C26, C32: 22µF; C_1210_3225Metric
C27, C29, C33, C42, C43: 100nF; C_0603_1608Metric
C31: 2.2µF; C_1206_3216Metric
D6: ESDS304; SOT-23-5
FB1, FB2: 300@100MHz; R_1206_3216Metric
J11: HFJ11-2450E-L21RL; RJ45_HALO_HFJ11-x2450E-LxxRL_Horizontal-Fixed3DModel
R14, R18: 10k; R_0603_1608Metric
R15, R17, R19, R20: 33; R_0603_1608Metric
R22: 6.49k; R_0603_1608Metric
R54, R55: 270; R_0603_1608Metric
R56: 4.7k; R_0603_1608Metric
U5: KSZ8081RND; QFN-24-1EP_4x4mm_P0.5mm_EP2.6x2.6mm

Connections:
/ETH_RMII.CRS_DV: R17.1, R18.2; also elsewhere on the board
/ETH_RMII.MDC: U5.11 (MDC); also elsewhere on the board
/ETH_RMII.MDIO: U5.10 (MDIO); also elsewhere on the board
/ETH_RMII.RMII_CLK: U5.8 (XI); also elsewhere on the board
/ETH_RMII.RXD0: R19.1; also elsewhere on the board
/ETH_RMII.RXD1: R20.1; also elsewhere on the board
/ETH_RMII.RX_ER: R14.2, R15.1; also elsewhere on the board
/ETH_RMII.TXD0: U5.20 (TXD0); also elsewhere on the board
/ETH_RMII.TXD1: U5.21 (TXD1); also elsewhere on the board
/ETH_RMII.TX_EN: U5.19 (TXEN); also elsewhere on the board
/EthernetInterface/ETH_MDI_RD+: D6.4 (K), J11.3 (RD+), U5.4 (RXP)
/EthernetInterface/ETH_MDI_RD-: D6.5 (K), J11.6 (RD-), U5.3 (RXM)
/EthernetInterface/ETH_MDI_TD+: D6.1 (K), J11.1 (TD+), U5.6 (TXP)
/EthernetInterface/ETH_MDI_TD-: D6.3 (K), J11.2 (TD-), U5.5 (TXM)
/EthernetInterface/KSZ_VDD1.2: C29.1, C31.1, U5.1 (VDD_1.2)
/EthernetInterface/~LED_GREEN: J11.12, R56.1, U5.23 (LED0/ANEN_SPEED)
/~ETH_SPEED_LED: J11.10; also elsewhere on the board
/~MCU_RST: U5.24 (~RST); also elsewhere on the board
GND: C26.1, C27.2, C29.2, C31.2, C32.1, C33.2, C42.2, C43.2, D6.2 (A), FB2.2, R14.1, R18.1, R22.1, U5.22 (GND), U5.25 (GND); also elsewhere on the board
unnamed: FB2.1, J11.8, J11.SH
unnamed: J11.9, R54.1
unnamed: J11.11, R55.1
unnamed: C43.1, J11.5 (RCT)
unnamed: C42.1, J11.4 (TCT)
unnamed: R17.2, U5.15 (CRS_DV/PHYAD[1:0])
unnamed: R22.2, U5.9 (REXT)
unnamed: R19.2, U5.13 (RXD0)
unnamed: R20.2, U5.12 (RXD1)
unnamed: R15.2, U5.17 (RXER)
unnamed: C32.2, C33.1, FB1.1, U5.2 (VDDA_3.3)

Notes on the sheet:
Green LED
Yellow LED
LED spec is 2.1V forward voltage @ 10mA. However, the KSZ8081 maxes out at 8mA of LED drive, and the MCU is similar. So, we will shoot for 5mA and assume that the forward voltage will decrease to around 2.0V
Per datasheet, RX_ER should be pulled low for correct operation (I guess it's an undocumented strapping pin?)
Ferrite bead per KSZ8081 reference design
CRS_DV pulled down to low and REF_CLK set high sets the PHY address to 4
Unfortunately there is only one LED pin on this PHY (it defaults to on for link up, flashing for activity). So, we will need to use the MCU to manually control the other (link speed) LED.
This part number of PHY is set up for MCUs like ours that can output a 50MHz clock. This clock is input to the PHY on the XI pin and is used both for the Ethernet signal generation and for the RMII interface. Look ma, no dedicated Ethernet crystal needed!

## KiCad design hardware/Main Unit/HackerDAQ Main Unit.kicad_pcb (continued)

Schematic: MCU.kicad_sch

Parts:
C5, C7, C8, C10, C15, C16, C17, C18, C19, C20, C22, C24, C25, C34: 100nF; C_0603_1608Metric
C6: 2.2µF; C_1206_3216Metric
C9, C14, C23: 1µF; C_0603_1608Metric
C11: 220nF; C_0603_1608Metric
C12, C13: 10µF; C_1206_3216Metric
D1: AA3528QBS; AA3528
D2: AA3528SURSK; AA3528
D3: ASMB-MTB0-0B3A2; LED_Avago_PLCC4_3.2x2.8mm_CW_Fixed3DModel
D4, D5: BAT54W; SOT-323_SC-70
J1: 3221-10-0300-00
J10: 1x8; PinSocket_1x08_P2.54mm_Vertical
J15: USB4105-GF-A; USB_C_Receptacle_GCT_USB4105-xx-A_16P_TopMnt_Horizontal-Ext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
L1: 1.5µH; L_1210_3225Metric
R1, R4, R7: 30; R_0603_1608Metric
R2, R3: 140; R_0603_1608Metric
R5, R6, R8, R23: 10k; R_0603_1608Metric
R9, R16: 2.2k; R_0603_1608Metric
R44, R45: 5.1k; R_0603_1608Metric
SW1, SW2: MJTP1243; SW_PUSH_1P1T_6x3.5mm_H4.3_APEM_MJTP1243
TP2: VCORE; TestPoint_THTPad_D2.5mm_Drill1.2mm
U4: MCXN547VKLT; LQFP-100-1EP_14x14mm_P0.5mm_EP6.9x6.9mm_Fixed3DModel
U11: USBLC6-2SC6; SOT-23-6
X1: 24.0000MHz; Oscillator_SMD_ECS_2520MV-xxx-xx-4Pin_2.5x2.0mm_Fixed3DModel

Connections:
/+3.3V_CUR_SENSE: U4.22 (P4_0); also elsewhere on the board
/CARD_BUS_0_SPI.CARD_SEL: U4.15 (P2_1); also elsewhere on the board
/CARD_BUS_0_SPI.MISO: U4.19 (P2_5); also elsewhere on the board
/CARD_BUS_0_SPI.MOSI: U4.18 (P2_4); also elsewhere on the board
/CARD_BUS_0_SPI.SCLK: U4.17 (P2_3); also elsewhere on the board
/CARD_BUS_0_SPI.~CS0: U4.16 (P2_2); also elsewhere on the board
/CARD_BUS_0_SPI.~CS1: U4.14 (P2_0); also elsewhere on the board
/CARD_BUS_0_SPI.~CS2: U4.21 (P2_7); also elsewhere on the board
/CARD_BUS_0_SPI.~DRDY: U4.20 (P2_6); also elsewhere on the board
/CARD_BUS_1_SPI.CARD_SEL: U4.91 (P0_23); also elsewhere on the board
/CARD_BUS_1_SPI.MISO: U4.3 (P1_10); also elsewhere on the board
/CARD_BUS_1_SPI.MOSI: U4.1 (P1_8); also elsewhere on the board
/CARD_BUS_1_SPI.SCLK: U4.2 (P1_9); also elsewhere on the board
/CARD_BUS_1_SPI.~CS0: U4.4 (P1_11); also elsewhere on the board
/CARD_BUS_1_SPI.~CS1: U4.90 (P0_22); also elsewhere on the board
/CARD_BUS_1_SPI.~CS2: U4.92 (P1_0); also elsewhere on the board
/CARD_BUS_1_SPI.~DRDY: U4.93 (P1_1); also elsewhere on the board
/CARD_BUS_2_SPI.CARD_SEL: U4.64 (P3_13); also elsewhere on the board
/CARD_BUS_2_SPI.MISO: U4.61 (P3_16); also elsewhere on the board
/CARD_BUS_2_SPI.MOSI: U4.63 (P3_14); also elsewhere on the board
/CARD_BUS_2_SPI.SCLK: U4.62 (P3_15); also elsewhere on the board
/CARD_BUS_2_SPI.~CS0: U4.60 (P3_17); also elsewhere on the board
/CARD_BUS_2_SPI.~CS1: U4.57 (P3_20); also elsewhere on the board
/CARD_BUS_2_SPI.~CS2: U4.56 (P3_21); also elsewhere on the board
/CARD_BUS_2_SPI.~DRDY: U4.75 (P3_0); also elsewhere on the board
/CARD_BUS_3_SPI.CARD_SEL: U4.50 (P5_2); also elsewhere on the board
/CARD_BUS_3_SPI.MISO: U4.69 (P3_9); also elsewhere on the board
/CARD_BUS_3_SPI.MOSI: U4.70 (P3_8); also elsewhere on the board
/CARD_BUS_3_SPI.SCLK: U4.71 (P3_7); also elsewhere on the board
/CARD_BUS_3_SPI.~CS0: U4.65 (P3_12); also elsewhere on the board
/CARD_BUS_3_SPI.~CS1: U4.78 (P0_2); also elsewhere on the board
/CARD_BUS_3_SPI.~CS2: U4.79 (P0_3); also elsewhere on the board
/CARD_BUS_3_SPI.~DRDY: U4.51 (P5_3); also elsewhere on the board
/Card Bus Connectors0/~RESET: U4.27 (P4_5); also elsewhere on the board
/Card Bus Connectors0/~SYNC: U4.28 (P4_6); also elsewhere on the board
/DBG_UART.MCU_RX: U4.35 (P4_12); also elsewhere on the board
/DBG_UART.MCU_TX: U4.36 (P4_13); also elsewhere on the board
/ETH_RMII.CRS_DV: U4.6 (P1_13); also elsewhere on the board
/ETH_RMII.MDC: U4.94 (P1_2); also elsewhere on the board
/ETH_RMII.MDIO: R16.2, U4.95 (P1_3); also elsewhere on the board
/ETH_RMII.RMII_CLK: U4.97 (P1_4); also elsewhere on the board
/ETH_RMII.RXD0: U4.7 (P1_14); also elsewhere on the board
/ETH_RMII.RXD1: U4.8 (P1_15); also elsewhere on the board
/ETH_RMII.RX_ER: U4.5 (P1_12); also elsewhere on the board
/ETH_RMII.TXD0: U4.99 (P1_6); also elsewhere on the board
/ETH_RMII.TXD1: U4.100 (P1_7); also elsewhere on the board
/ETH_RMII.TX_EN: U4.98 (P1_5); also elsewhere on the board
/MCU/+5V_CUR_SENSE: U4.23 (P4_1); also elsewhere on the board
/MCU/CLK_24MHZ: U4.10 (EXTAL48M/P1_31), X1.3 (OUT)
/MCU/ERROR_LED: R2.2, U4.26 (P4_4)
/MCU/MCU_P0_4: J10.1, U4.80 (P0_4)
/MCU/MCU_P0_5: J10.2, U4.81 (P0_5)
/MCU/MCU_P0_16: J10.3, U4.84 (P0_16)
/MCU/MCU_P0_17: J10.4, U4.85 (P0_17)
/MCU/MCU_P0_18: J10.5, U4.86 (P0_18)
/MCU/MCU_P0_19: J10.6, U4.87 (P0_19)
/MCU/MCU_P0_20: J10.7, U4.88 (P0_20)
/MCU/MCU_P0_21: J10.8, U4.89 (P0_21)
/MCU/PREFILT_USBMCU_D+: J15.A6 (D+), J15.B6 (D+), U11.3 (I/O2)
/MCU/PREFILT_USBMCU_D-: J15.A7 (D-), J15.B7 (D-), U11.1 (I/O1)
/MCU/RGB_LED_~B: R7.2, U4.39 (P4_17)
/MCU/RGB_LED_~G: R4.2, U4.38 (P4_16)
/MCU/RGB_LED_~R: R3.2, U4.37 (P4_15)
/MCU/STATUS_LED: R1.1, U4.25 (P4_3)
/MCU/SWCLK: J1.4, R5.2, U4.77 (SWCLK/P0_1/TCLK)
/MCU/SWDIO: J1.2, R6.1, U4.76 (SWDIO/P0_0/TMS)
/MCU/USBMCU_D+: U4.40 (USB1_DP), U11.4 (I/O2)
/MCU/USBMCU_D-: U4.41 (USB1_DM), U11.6 (I/O1)
/MCU/USBMCU_VBUS: J15.A4 (VBUS), J15.A9 (VBUS), J15.B4 (VBUS), J15.B9 (VBUS), U4.42 (USB1_VBUS), U11.5 (VBUS)
/MCU/VDD_SYS: C6.1, U4.55 (VDD_SYS)
/MCU/~ISPMODE: C34.1, D5.1 (A), R23.1, SW2.2, U4.82 (ISPMODE_N/P0_6)
/V_{SUPPLY}_CUR_SENSE: U4.24 (P4_2); also elsewhere on the board
/uSD_SPI.MISO: U4.68 (P3_10); also elsewhere on the board
/uSD_SPI.MOSI: U4.74 (P3_1); also elsewhere on the board
/uSD_SPI.SCLK: U4.72 (P3_6); also elsewhere on the board
/uSD_SPI.~CS: U4.67 (P3_11); also elsewhere on the board
/~ETH_SPEED_LED: U4.48 (P5_0); also elsewhere on the board
/~MCU_RST: C5.1, D4.1 (A), J1.10, R8.1, R9.1, SW1.2; also elsewhere on the board
/~SD_CARD_EN: U4.49 (P5_1); also elsewhere on the board
GND: C5.2, C6.2, C7.2, C8.2, C9.2, C10.2, C11.2, C12.1, C13.1, C14.2, C15.2, C16.2, C17.2, C18.2, C19.2, C20.2, C22.2, C23.2, C24.2, C25.2, C34.2, D1.1 (K), D2.1 (K), J1.3, J1.5, J15.A1 (GND), J15.A12 (GND), J15.B1 (GND), J15.B12 (GND), R5.1, R44.1, R45.1, SW1.1, SW2.1, U4.32 (VREFL), U4.33 (VSS_P4), U4.43 (VSS), U4.52 (VSS_DCDC), U4.101 (VSS), U11.2 (GND), X1.2 (GND); also elsewhere on the board
unnamed: D1.2 (A), R1.2
unnamed: D2.2 (A), R2.1
unnamed: D3.2 (BK), R7.1
unnamed: D3.3 (GK), R4.1
unnamed: D3.4 (RK), R3.1
unnamed: J15.A5 (CC1), R44.2
unnamed: J15.B5 (CC2), R45.2
unnamed: L1.1, U4.53 (DCDC_LX)
unnamed: C11.1, U4.29 (P4_7/VREFI/VREFO)
unnamed: R9.2, U4.9 (RESET_B)

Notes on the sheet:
RTCK
GNDDetect
TMS/SWDIO
VTREF
~RST
Route per hardware design guide:
Expansion Header
GND
TDI
TDO/SWO
TCLK/SWCLK
Reset circuit. Can be pulled low from the pushbutton or the JTAG connector. Also pulled low at startup by the MCU during its power-on reset. The diode exists to discharge the capacitor when power is turned off.
Note: Decoupling per hardware design guide. Generally each group of pins gets one large capacitor, and each pin gets a smaller capacitor
Main CPU clock source. Yeah we could get away with using the internal oscillator to drive the CPU core, but it's not accurate enough for Ethernet so we'd still need a crystal oscillator. So why not plonk down a TCXO and enjoy +-5ppm accurate clocks for everything?
Using the remaining 5 free GPIOs for indicator LEDs
Per datasheet VDD_P4 and VDD_ANA must be powered by the same supply.
SWD debug connector. Not using JTAG as it's not worth the two extra pins for no additional benefit. Resistors on SWDIO and SWCLK are per hardware design guide recommendation.
This tricolor LED specifies V_{F} = 2.1V (red) and 3.1V (green and blue) @ 20mA. Making a ballpark assumption that the forward voltage decreases by 0.1V if we reduce the forward current to 10mA.
ISP mode circuit. Button can be pressed to force the MCU to boot into ISP (recovery) mode.

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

Board: 4 copper layers, 244.5 x 91.0 mm, 186 parts (0 on the bottom side), 187 nets.

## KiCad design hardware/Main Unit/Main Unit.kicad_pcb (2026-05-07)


Board: 4 copper layers, 244.5 x 91.0 mm, 151 parts (0 on the bottom side), 165 nets.

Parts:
C1, C3, C4, C5, C6, C8, C9, C11, C12, C13, C17, C19, C20, C21, C22, C23, C25, C26, C27, C33, C34, C36, C37, C38, C40, C41, C45, C46, C50, C52, C53, C55: 100nF; C_0603_1608Metric
C2, C7, C10, C24, C28, C29, C31, C54: 1µF; C_0603_1608Metric
C14, C35: 2.2µF; C_1206_3216Metric
C15, C16, C30, C32, C51, C56: 10µF; C_1206_3216Metric
C18: 220nF; C_0603_1608Metric
C39, C42, C47, C48: 22µF; C_1210_3225Metric
C43, C44: 10µF; C_1210_3225Metric
C49: 150pF; C_0603_1608Metric
D1, D2: BAT54W; SOT-323_SC-70
D3: AA3528SYSK; AA3528
D4: AA3528QBS; AA3528
D5: AA3528CGSK; AA3528
D6: ESDS304; SOT-23-5
D7: SMF24A; D_SMF
FB1, FB6: 300@100MHz; R_1206_3216Metric
J1: 3221-10-0300-00
J2, J3, J4, J5, J6, J7, J8, J9: 61801525123; Wurth_61801525123
J10: DM3AT; microSD_HC_Hirose_DM3AT-SF-PEJM5
J11, J12: USB4105-GF-A; USB_C_Receptacle_GCT_USB4105-xx-A_16P_TopMnt_Horizontal-Ext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
J13: HFJ11-2450E-L21RL; RJ45_HALO_HFJ11-x2450E-LxxRL_Horizontal-Fixed3DModel
J14: PJ-063AH; BarrelJack_CUI_PJ-063AH_Horizontal
J15: 0039300020; Molex_Mini-Fit_Jr_5569-02A2_2x01_P4.20mm_Horizontal
J16: 1x8; PinSocket_1x08_P2.54mm_Vertical
L1: 1.5µH; L_1210_3225Metric
L2: 2.2μH; 0630CDMCDDS
LG1: HackerDAQ Logo
R1, R18: 2.2k; R_0603_1608Metric
R2, R3, R4, R10, R11, R22, R23, R28, R29, R36: 10k; R_0603_1608Metric
R5, R6, R7, R8, R12: 10k; CTS 745C101
R9: 1k; R_0603_1608Metric
R13, R14, R16, R17, R34: 33; R_0603_1608Metric
R15, R19, R41, R42: 5.1k; R_0603_1608Metric
R20, R37: 140; R_0603_1608Metric
R21: 30; R_0603_1608Metric
R24, R25: 4.7k; R_0603_1608Metric
R26, R27: 270; R_0603_1608Metric
R30: 6.49k; R_0603_1608Metric
R31: 52.3k; R_0603_1608Metric
R32: 18.2k; R_0603_1608Metric
R33: 3.01k; R_0603_1608Metric
R35: 45.3k; R_0603_1608Metric
R38, R43: .0025; D1FCP0612
R39, R40, R44, R45: 10; R_0603_1608Metric
SW1, SW2: MJTP1243; SW_PUSH_1P1T_6x3.5mm_H4.3_APEM_MJTP1243
TP1: VCORE; TestPoint_THTPad_D2.5mm_Drill1.2mm
TP2: +3.3VA; TestPoint_THTPad_D2.5mm_Drill1.2mm
TP3: +3.3V; TestPoint_THTPad_D2.5mm_Drill1.2mm
U1: MCXN547VKLT; LQFP-100-1EP_14x14mm_P0.5mm_EP6.9x6.9mm_Fixed3DModel
U2: TLV71333PDBV; SOT-23-5
U3, U4, U5, U6: SN74CB3Q3257PWR; TSSOP-16_4.4x5mm_P0.65mm
U7: KSZ8081RND; QFN-24-1EP_4x4mm_P0.5mm_EP2.65x2.65mm-LengthenedPads
U8: AP22913W6-7; SOT-23-6
U9: SN74AXC4T774; TSSOP-16_4.4x5mm_P0.65mm
U10, U13: USBLC6-2SC6; SOT-23-6
U11: TPS56A37RPAR; RPA0010A-MFG
U12, U15: INA180A3; SOT-23-5
U14: CY7C65223; QFN-24-1EP_4x4mm_P0.5mm_EP2.65x2.65mm-LengthenedPads
X1: 24.0000MHz; Oscillator_SMD_ECS_2520MV-xxx-xx-4Pin_2.5x2.0mm
X2: 8.192MHz; Oscillator_SMD_ECS_2520MV-xxx-xx-4Pin_2.5x2.0mm

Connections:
+3.3V: C3.1, C4.1, C5.1, C6.1, C7.1, C8.1, C9.1, C16.2, C17.1, C21.1, C22.1, C23.1, C24.1, C25.1, C26.1, C27.1, C29.1, C30.2, C34.1, C41.1, C42.2, C50.1, C52.1, C53.1, D1.3 (K), D2.3 (K), FB1.2, J1.1, J2.5, J3.5, J4.5, J5.5, J6.5, J7.5, J8.5, J9.5, R2.2, R3.2, R5.5 (common), R5.10 (common), R6.5 (common), R6.10 (common), R7.5 (common), R7.10 (common), R8.5 (common), R8.10 (common), R9.2, R18.1, R20.1, R21.1, R23.2, R25.2, R26.2, R27.2, R37.1, R38.1, TP3.1, U1.13 (VDD/VDD_LDO_CORE/VDD_P2), U1.44 (VDD_USB), U1.47 (VDD_BAT), U1.54 (VDD_DCDC/VDD_LDO_SYS), U1.59 (VDD_P3), U1.66 (VDD_P3), U1.73 (VDD_P3), U1.83 (VDD), U1.96 (VDD), U3.16 (VCC), U4.16 (VCC), U5.16 (VCC), U6.16 (VCC), U7.14 (VDDIO), U7.16 (REF_CLK), U8.4 (VIN), U8.6 (VIN), U9.1 (DIR1), U9.2 (DIR2), U9.7 (DIR3), U9.16 (VCCA), U12.5 (V+), U14.15 (VBUS), U14.24 (VDDD), X1.1 (Tri-State), X1.4 (VDD), X2.1 (Tri-State), X2.4 (VDD)
+3.3VA: C2.1, C10.1, C11.1, TP2.1, U1.30 (VDD_ANA), U1.31 (VREFH), U1.34 (VDD_P4), U2.5 (OUT)
+5V: C1.1, J2.3, J3.3, J4.3, J5.3, J6.3, J7.3, J8.3, J9.3, U2.1 (IN)
/8.192MHZ_CLK: J2.4, J3.4, J4.4, J5.4, J6.4, J7.4, J8.4, J9.4, X2.3 (OUT)
/+3.3V_CUR_SENSE: U1.37 (P4_15), U12.1
/CARD_BUS_0_SPI.CARD_SEL: U1.15 (P2_1), U4.1 (S)
/CARD_BUS_0_SPI.MISO: J4.12, J5.12, U1.19 (P2_5)
/CARD_BUS_0_SPI.MOSI: J4.13, J5.13, U1.18 (P2_4)
/CARD_BUS_0_SPI.SCLK: J4.14, J5.14, U1.17 (P2_3)
/CARD_BUS_0_SPI.~CS0: U1.16 (P2_2), U4.4 (1A)
/CARD_BUS_0_SPI.~CS1: U1.14 (P2_0), U4.7 (2A)
/CARD_BUS_0_SPI.~CS2: U1.21 (P2_7), U4.9 (3A)
/CARD_BUS_0_SPI.~DRDY: J4.10, J5.10, U1.20 (P2_6)
/CARD_BUS_1_SPI.CARD_SEL: U1.91 (P0_23), U3.1 (S)
/CARD_BUS_1_SPI.MISO: J2.12, J3.12, U1.3 (P1_10)
/CARD_BUS_1_SPI.MOSI: J2.13, J3.13, U1.1 (P1_8)
/CARD_BUS_1_SPI.SCLK: J2.14, J3.14, U1.2 (P1_9)
/CARD_BUS_1_SPI.~CS0: U1.4 (P1_11), U3.4 (1A)
/CARD_BUS_1_SPI.~CS1: U1.90 (P0_22), U3.7 (2A)
/CARD_BUS_1_SPI.~CS2: U1.92 (P1_0), U3.9 (3A)
/CARD_BUS_1_SPI.~DRDY: J2.10, J3.10, U1.93 (P1_1)
/CARD_BUS_2_SPI.CARD_SEL: U1.64 (P3_13), U5.1 (S)
/CARD_BUS_2_SPI.MISO: J6.12, J7.12, U1.61 (P3_16)
/CARD_BUS_2_SPI.MOSI: J6.13, J7.13, U1.63 (P3_14)
/CARD_BUS_2_SPI.SCLK: J6.14, J7.14, U1.62 (P3_15)
/CARD_BUS_2_SPI.~CS0: U1.60 (P3_17), U5.4 (1A)
/CARD_BUS_2_SPI.~CS1: U1.57 (P3_20), U5.7 (2A)
/CARD_BUS_2_SPI.~CS2: U1.56 (P3_21), U5.9 (3A)
/CARD_BUS_2_SPI.~DRDY: J6.10, J7.10, U1.75 (P3_0)
/CARD_BUS_3_SPI.CARD_SEL: U1.50 (P5_2), U6.1 (S)
/CARD_BUS_3_SPI.MISO: J8.12, J9.12, U1.69 (P3_9)
/CARD_BUS_3_SPI.MOSI: J8.13, J9.13, U1.70 (P3_8)
/CARD_BUS_3_SPI.SCLK: J8.14, J9.14, U1.71 (P3_7)
/CARD_BUS_3_SPI.~CS0: U1.65 (P3_12), U6.4 (1A)
/CARD_BUS_3_SPI.~CS1: U1.78 (P0_2), U6.7 (2A)
/CARD_BUS_3_SPI.~CS2: U1.79 (P0_3), U6.9 (3A)
/CARD_BUS_3_SPI.~DRDY: J8.10, J9.10, U1.51 (P5_3)
/Card Bus Connectors0/F_CARD_CS.~CS0: J5.8, R6.2 (R2), U4.3 (1B2)
/Card Bus Connectors0/F_CARD_CS.~CS1: J5.15, R6.3 (R3), U4.6 (2B2)
/Card Bus Connectors0/F_CARD_CS.~CS2: J5.7, R6.4 (R4), U4.10 (3B2)
/Card Bus Connectors0/L_CARD_CS.~CS0: J4.8, R6.8 (R7), U4.2 (1B1)
/Card Bus Connectors0/L_CARD_CS.~CS1: J4.15, R6.7 (R6), U4.5 (2B1)
/Card Bus Connectors0/L_CARD_CS.~CS2: J4.7, R6.6 (R5), U4.11 (3B1)
/Card Bus Connectors0/~RESET: J2.6, J3.6, J4.6, J5.6, J6.6, J7.6, J8.6, J9.6, U1.27 (P4_5)
/Card Bus Connectors0/~SYNC: J2.11 (P111), J3.11 (P111), J4.11 (P111), J5.11 (P111), J6.11 (P111), J7.11 (P111), J8.11 (P111), J9.11 (P111), U1.28 (P4_6)
/Card Bus Connectors1/F_CARD_CS.~CS0: J3.8, R5.2 (R2), U3.3 (1B2)
/Card Bus Connectors1/F_CARD_CS.~CS1: J3.15, R5.3 (R3), U3.6 (2B2)
/Card Bus Connectors1/F_CARD_CS.~CS2: J3.7, R5.4 (R4), U3.10 (3B2)
/Card Bus Connectors1/L_CARD_CS.~CS0: J2.8, R5.8 (R7), U3.2 (1B1)
/Card Bus Connectors1/L_CARD_CS.~CS1: J2.15, R5.7 (R6), U3.5 (2B1)
/Card Bus Connectors1/L_CARD_CS.~CS2: J2.7, R5.6 (R5), U3.11 (3B1)
/Card Bus Connectors2/F_CARD_CS.~CS0: J7.8, R7.2 (R2), U5.3 (1B2)
/Card Bus Connectors2/F_CARD_CS.~CS1: J7.15, R7.3 (R3), U5.6 (2B2)
/Card Bus Connectors2/F_CARD_CS.~CS2: J7.7, R7.4 (R4), U5.10 (3B2)
/Card Bus Connectors2/L_CARD_CS.~CS0: J6.8, R7.8 (R7), U5.2 (1B1)
/Card Bus Connectors2/L_CARD_CS.~CS1: J6.15, R7.7 (R6), U5.5 (2B1)
/Card Bus Connectors2/L_CARD_CS.~CS2: J6.7, R7.6 (R5), U5.11 (3B1)
/Card Bus Connectors3/F_CARD_CS.~CS0: J9.8, R8.2 (R2), U6.3 (1B2)
/Card Bus Connectors3/F_CARD_CS.~CS1: J9.15, R8.3 (R3), U6.6 (2B2)
/Card Bus Connectors3/F_CARD_CS.~CS2: J9.7, R8.4 (R4), U6.10 (3B2)
/Card Bus Connectors3/L_CARD_CS.~CS0: J8.8, R8.8 (R7), U6.2 (1B1)
/Card Bus Connectors3/L_CARD_CS.~CS1: J8.15, R8.7 (R6), U6.5 (2B1)
/Card Bus Connectors3/L_CARD_CS.~CS2: J8.7, R8.6 (R5), U6.11 (3B1)
/DBG_UART.MCU_RX: U1.35 (P4_12), U14.23 (TxD)
/DBG_UART.MCU_TX: U1.36 (P4_13), U14.1 (RxD)
/DebugUSBUART/MCU_RX_LED: D3.1 (K), U14.18 (TXLED_0)
/DebugUSBUART/MCU_TX_LED: D4.1 (K), U14.19 (RXLED_0)
/DebugUSBUART/PREFILT_USBSER_D+: J11.A6 (D+), J11.B6 (D+), U10.3 (I/O2)
/DebugUSBUART/PREFILT_USBSER_D-: J11.A7 (D-), J11.B7 (D-), U10.1 (I/O1)
/DebugUSBUART/USBSER_D+: U10.4 (I/O2), U14.10 (USBDP)
/DebugUSBUART/USBSER_D-: U10.6 (I/O1), U14.11 (USBDM)
/DebugUSBUART/USBSER_VBUS: J11.A4 (VBUS), J11.A9 (VBUS), J11.B4 (VBUS), J11.B9 (VBUS), R24.2, U10.5 (VBUS)
/DebugUSBUART/USBSER_VCCD: C54.1, U14.12 (VCCD)
/DebugUSBUART/USBSER_XRES: R22.2, R24.1, U14.14 (~XRES)
/ETH_RMII.CRS_DV: R16.1, R29.2, U1.6 (P1_13)
/ETH_RMII.MDC: U1.94 (P1_2), U7.11 (MDC)
/ETH_RMII.MDIO: R18.2, U1.95 (P1_3), U7.10 (MDIO)
/ETH_RMII.RMII_CLK: U1.97 (P1_4), U7.8 (XI)
/ETH_RMII.RXD0: R13.1, U1.7 (P1_14)
/ETH_RMII.RXD1: R14.1, U1.8 (P1_15)
/ETH_RMII.RX_ER: R17.1, R28.2, U1.5 (P1_12)
/ETH_RMII.TXD0: U1.99 (P1_6), U7.20 (TXD0)
/ETH_RMII.TXD1: U1.100 (P1_7), U7.21 (TXD1)
/ETH_RMII.TX_EN: U1.98 (P1_5), U7.19 (TXEN)
/EthernetInterface/ETH_MDI_RD+: D6.4 (K), J13.3 (RD+), U7.4 (RXP)
/EthernetInterface/ETH_MDI_RD-: D6.5 (K), J13.6 (RD-), U7.3 (RXM)
/EthernetInterface/ETH_MDI_TD+: D6.1 (K), J13.1 (TD+), U7.6 (TXP)
/EthernetInterface/ETH_MDI_TD-: D6.3 (K), J13.2 (TD-), U7.5 (TXM)
/EthernetInterface/KSZ_VDD1.2: C35.1, C36.1, U7.1 (VDD_1.2)
/EthernetInterface/~LED_GREEN: J13.12, R25.1, U7.23 (LED0/ANEN_SPEED)
/MCU/CLK_24MHZ: U1.10 (EXTAL48M/P1_31), X1.3 (OUT)
/MCU/MCU_P0_4: J16.1, U1.80 (P0_4)
/MCU/MCU_P0_5: J16.2, U1.81 (P0_5)
/MCU/MCU_P0_16: J16.3, U1.84 (P0_16)
/MCU/MCU_P0_17: J16.4, U1.85 (P0_17)
/MCU/MCU_P0_18: J16.5, U1.86 (P0_18)
/MCU/MCU_P0_19: J16.6, U1.87 (P0_19)
/MCU/MCU_P0_20: J16.7, U1.88 (P0_20)
/MCU/MCU_P0_21: J16.8, U1.89 (P0_21)
/MCU/PREFILT_USBMCU_D+: J12.A6 (D+), J12.B6 (D+), U13.3 (I/O2)
/MCU/PREFILT_USBMCU_D-: J12.A7 (D-), J12.B7 (D-), U13.1 (I/O1)
/MCU/SWCLK: J1.4, R4.2, U1.77 (SWCLK/P0_1/TCLK)
/MCU/SWDIO: J1.2, R3.1, U1.76 (SWDIO/P0_0/TMS)
/MCU/USBMCU_D+: U1.40 (USB1_DP), U13.4 (I/O2)
/MCU/USBMCU_D-: U1.41 (USB1_DM), U13.6 (I/O1)
/MCU/USBMCU_VBUS: J12.A4 (VBUS), J12.A9 (VBUS), J12.B4 (VBUS), J12.B9 (VBUS), U1.42 (USB1_VBUS), U13.5 (VBUS)
/MCU/VCORE: C12.1, C13.1, C15.2, L1.2, TP1.1, U1.12 (VDD_CORE), U1.58 (VDD_CORE)
/MCU/VDD_SYS: C14.1, U1.55 (VDD_SYS)
/MCU/~ISPMODE: C20.1, D2.1 (A), R2.1, SW2.2, U1.82 (ISPMODE_N/P0_6)
/MicroSDCard/+3.3V@SD: C31.1, C32.2, C33.1, J10.4 (VDD), R12.5 (common), R12.10 (common), U8.1 (OUT), U9.15 (VCCB)
/MicroSDCard/CLK@SD: J10.5 (CLK), R11.2, U9.12 (B3)
/MicroSDCard/CMD_MOSI@SD: J10.3 (CMD), R12.2 (R2), U9.13 (B2)
/MicroSDCard/DAT0_MISO@SD: J10.7 (DAT0), R12.3 (R3), U9.11 (B4)
/MicroSDCard/DET_A: J10.10 (DET_A), R9.1
/MicroSDCard/DET_B: C28.1, J10.9 (DET_B), R10.2, U8.3 (ON)
/MicroSDCard/~CS@SD: J10.2 (DAT3/CD), R12.1 (R1), U9.14 (B1)
/SupplyTo3.3VRegulator/+3.3V_PRE_SENSE: C47.2, C48.2, C49.2, L2.2, R35.2, R38.4
/SupplyTo3.3VRegulator/BOOT: C46.1, U11.7 (BOOT)
/SupplyTo3.3VRegulator/EN: R32.1, R33.2, U11.1 (EN)
/SupplyTo3.3VRegulator/FB: C49.1, R35.1, R36.1, U11.2 (FB)
/SupplyTo3.3VRegulator/SW: C46.2, L2.1, U11.6 (SW)
/V_{SUPPLY} Input/V_{SUPPLY}_IN: D7.1 (A1), J14.1, J15.2, R43.4
/V_{SUPPLY}_CUR_SENSE: U1.39 (P4_17), U15.1
/uSD_SPI.MISO: R34.1, U1.68 (P3_10)
/uSD_SPI.MOSI: U1.74 (P3_1), U9.4 (A2)
/uSD_SPI.SCLK: U1.72 (P3_6), U9.5 (A3)
/uSD_SPI.~CS: U1.67 (P3_11), U9.3 (A1)
/~ETH_SPEED_LED: J13.10, U1.48 (P5_0)
/~MCU_RST: C19.1, D1.1 (A), J1.10, R1.1, R23.1, SW1.2, U2.3 (EN), U7.24 (~RST), U11.4 (PG)
/~SD_CARD_EN: U1.49 (P5_1), U9.9 (~OE)
GND: C1.2, C2.2, C3.2, C4.2, C5.2, C6.2, C7.2, C8.2, C9.2, C10.2, C11.2, C12.2, C13.2, C14.2, C15.1, C16.1, C17.2, C18.2, C19.2, C20.2, C21.2, C22.2, C23.2, C24.2, C25.2, C26.2, C27.2, C28.2, C29.2, C30.1, C31.2, C32.1, C33.2, C34.2, C35.2, C36.2, C37.2, C38.2, C39.1, C40.2, C41.2, C42.1, C43.1, C44.1, C45.2, C47.1, C48.1, C50.2, C52.2, C53.2, C54.2, C55.2, D5.1 (K), D6.2 (A), D7.2 (A2), FB6.2, J1.3, J1.5, J2.0 (PAD), J2.2, J2.9, J3.0 (PAD), J3.2, J3.9, J4.0 (PAD), J4.2, J4.9, J5.0 (PAD), J5.2, J5.9, J6.0 (PAD), J6.2, J6.9, J7.0 (PAD), J7.2, J7.9, J8.0 (PAD), J8.2, J8.9, J9.0 (PAD), J9.2, J9.9, J10.6 (VSS), J10.11 (SHIELD), J11.A1 (GND), J11.A12 (GND), J11.B1 (GND), J11.B12 (GND), J12.A1 (GND), J12.A12 (GND), J12.B1 (GND), J12.B12 (GND), J14.2, J15.1, R4.1, R10.1, R11.1, R15.1, R19.1, R22.1, R28.1, R29.1, R30.1, R31.1, R33.1, R36.2, R41.1, R42.1, SW1.1, SW2.1, U1.32 (VREFL), U1.33 (VSS_P4), U1.43 (VSS), U1.52 (VSS_DCDC), U1.101 (VSS), U2.2 (GND), U3.8 (GND), U3.12 (4A), U3.15 (~OE), U4.8 (GND), U4.12 (4A), U4.15 (~OE), U5.8 (GND), U5.12 (4A), U5.15 (~OE), U6.8 (GND), U6.12 (4A), U6.15 (~OE), U7.22 (GND), U7.25 (GND), U8.2 (GND), U8.5 (GND), U9.8 (DIR4), U9.10 (GND), U10.2 (GND), U11.3 (AGND), U11.9 (PGND), U12.2 (GND), U13.2 (GND), U14.3 (VSSD), U14.5 (GPIO_9), U14.9 (WAKEUP), U14.13 (VSSD), U14.16 (VSSD), U14.17 (VSSA), U14.20 (~DSR), U14.22 (~CTS), U14.25 (GND), U15.2 (GND), X1.2 (GND), X2.2 (GND)
unnamed: D3.2 (A), R20.2
unnamed: D4.2 (A), R21.2
unnamed: D5.2 (A), R37.2
unnamed: FB6.1, J13.8, J13.SH
unnamed: J10.8 (DAT1), R12.7 (R6)
unnamed: J10.1 (DAT2), R12.6 (R5)
unnamed: J11.A5 (CC1), R15.2
unnamed: J11.B5 (CC2), R19.2
unnamed: J12.A5 (CC1), R41.2
unnamed: J12.B5 (CC2), R42.2
unnamed: J13.9, R27.1
unnamed: J13.11, R26.1
unnamed: C38.1, J13.5 (RCT)
unnamed: C37.1, J13.4 (TCT)
unnamed: R38.2, R40.1
unnamed: R38.3, R39.1
unnamed: R43.2, R45.1
unnamed: R43.3, R44.1
unnamed: L1.1, U1.53 (DCDC_LX)
unnamed: C18.1, U1.29 (P4_7/VREFI/VREFO)
unnamed: R1.2, U1.9 (RESET_B)
unnamed: R16.2, U7.15 (CRS_DV/PHYAD[1:0])
unnamed: R30.2, U7.9 (REXT)
unnamed: R13.2, U7.13 (RXD0)
unnamed: R14.2, U7.12 (RXD1)
unnamed: R17.2, U7.17 (RXER)
unnamed: C39.2, C40.1, FB1.1, U7.2 (VDDA_3.3)
unnamed: R34.2, U9.6 (A4)
unnamed: R31.2, U11.10 (MODE)
unnamed: C51.2, R39.2, U12.3 (+)
unnamed: C51.1, R40.2, U12.4 (-)
unnamed: C56.2, R44.2, U15.3 (+)
unnamed: C56.1, R45.2, U15.4 (-)
V_{SUPPLY}: C43.2, C44.2, C45.1, C55.1, J2.1, J3.1, J4.1, J5.1, J6.1, J7.1, J8.1, J9.1, R32.2, R43.1, U11.8 (VIN), U15.5 (V+)

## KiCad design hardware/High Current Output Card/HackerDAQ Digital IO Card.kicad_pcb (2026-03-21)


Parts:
J1, J2, J3: MiniFit_Jr_5569_08A2; Molex_Mini-Fit_Jr_5569-08A2_2x04_P4.20mm_Horizontal
LG1: HackerDAQ Logo

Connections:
+3.3V: J1.4; also elsewhere on the board
+5V: J1.8; also elsewhere on the board
+V_SUPPLY: J1.5; also elsewhere on the board
/DIOA0: J2.5; also elsewhere on the board
/DIOA2: J2.7; also elsewhere on the board
/DIOA3: J2.8; also elsewhere on the board
/DIOB0: J3.5; also elsewhere on the board
/DIOB1: J3.6; also elsewhere on the board
/DIOB2: J3.7; also elsewhere on the board
/DIOB3: J3.8; also elsewhere on the board
/V_{LOGIC}_PORTB: J1.2; also elsewhere on the board
GND: J1.3, J1.7, J2.1, J2.2, J2.3, J2.4, J3.1, J3.2, J3.3, J3.4; also elsewhere on the board

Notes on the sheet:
V_{LOGIC} Selection
Digital Front Ends (Port B)
Main Board Interface
Digital Front Ends (Port A)
I/O Expanders
Identity EEPROM
User can select Vlogic for each bank via attaching a jumper to this connector. 3.3V, 5V, or Vsupply can be used, or an external logic voltage can be fed in. Mini-Fit connectors are rated for about 5-7A per pin, so to hit the full rated current you will need to supply external Vlogic on both pins.

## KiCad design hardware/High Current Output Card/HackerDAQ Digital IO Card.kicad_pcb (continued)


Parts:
C6, C12: 100nF; C_0603_1608Metric
C7, C8, C9, C11: 1µF; C_0603_1608Metric
D1: AA3528SURSK; AA3528
Q6, Q9, Q10: 2N7002; SOT-23
Q7, Q8: RVQ040N05; SOT-23-6
R12: 150; R_1206_3216Metric
R13, R27: 10k; R_0603_1608Metric
R14: 75k; R_0603_1608Metric
R16, R17: 2.2; R_0603_1608Metric
R18: 30k; R_0603_1608Metric
R19, R24: 133k; R_0603_1608Metric
R20: 14.7k; R_0603_1608Metric
R21, R22: 1; R_0603_1608Metric
R25: 33.2k; R_0603_1608Metric
U5: LM311DR; SOIC-8_3.9x4.9mm_P1.27mm
U7, U8: RT9624CGQWA; DFN-8-1EP_2x2mm_P0.5mm_EP0.6x1.2mm_LeadsExtended
U9: LM358; TSSOP-8_3x3mm_P0.65mm

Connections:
+5V: C6.1, R12.1, R13.2, R16.1, R17.1, U5.8 (V+), U7.3 (EN), U8.3 (EN); also elsewhere on the board
/DIG_IN_A1: Q6.1 (G), R13.1, R14.1, U5.7; also elsewhere on the board
/DigitalIODriverA1/HICUR_LGATE: Q8.3 (G), U7.5 (LGATE)
/DigitalIODriverA1/HICUR_UGATE: Q7.3 (G), U7.8 (UGATE)
/DigitalIODriverA1/PULL_LGATE: Q10.1 (G), U8.5 (LGATE)
/DigitalIODriverA1/PULL_PHASE: C11.2, Q9.2 (S), Q10.3 (D), R27.1, U8.7 (PHASE)
/DigitalIODriverA1/PULL_UGATE: Q9.1 (G), U8.8 (UGATE)
/DigitalIODriverA1/V_{LOGIC}/10: R19.2, R20.1, U5.3 (-)
/HICUR_LOGIC_CTRL_A1: U7.2 (PWM); also elsewhere on the board
/PULL_LOGIC_CTRL_A1: U8.2 (PWM); also elsewhere on the board
GND: C6.2, C7.2, C8.2, C12.2, Q6.3 (D), Q8.4 (S), Q10.2 (S), R20.2, R25.2, U5.1 (GND), U5.4 (V-), U7.6 (GND), U7.9 (GND), U8.6 (GND), U8.9 (GND), U9.4 (V-); also elsewhere on the board
unnamed: C9.1, R21.2
unnamed: C11.1, R22.2
unnamed: D1.2 (A), R12.2
unnamed: D1.1 (K), Q6.2 (S)
unnamed: R14.2, R18.2, U5.2 (+)
unnamed: R21.1, U7.1 (BOOT)
unnamed: C7.1, R16.2, U7.4 (VCC)
unnamed: R22.1, U8.1 (BOOT)
unnamed: C8.1, R17.2, U8.4 (VCC)
unnamed: R24.2, R25.1, U9.5 (+)

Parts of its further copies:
C1, C2, C3, C10, C14, C15, C16, C17, C20, C21, C22, C23, C26, C27, C28, C29, C33, C34, C35, C36, C39, C40, C41, C42, C45, C46, C47, C48: 1µF; C_0603_1608Metric
C4, C13, C18, C19, C24, C25, C30, C32, C37, C38, C43, C44, C49: 100nF; C_0603_1608Metric
D2, D3, D4, D5, D6, D7, D8: AA3528SURSK; AA3528
Q1, Q2, Q12, Q13, Q17, Q18, Q22, Q23, Q27, Q28, Q32, Q33, Q37, Q38: RVQ040N05; SOT-23-6
Q3, Q4, Q5, Q11, Q14, Q15, Q16, Q19, Q20, Q21, Q24, Q25, Q26, Q29, Q30, Q31, Q34, Q35, Q36, Q39, Q40: 2N7002; SOT-23
R1, R3, R31, R32, R44, R45, R57, R58, R70, R71, R83, R84, R96, R97: 2.2; R_0603_1608Metric
R2, R15, R36, R37, R49, R50, R62, R63, R75, R76, R88, R89, R101, R102: 1; R_0603_1608Metric
R4, R30, R43, R56, R69, R82, R95: 75k; R_0603_1608Metric
R5, R46, R59, R72, R85, R98: 30k; R_0603_1608Metric
R6, R23, R29, R40, R42, R53, R55, R66, R68, R79, R81, R92, R94, R105: 10k; R_0603_1608Metric
R7, R39, R52, R65, R78, R91, R104: 33.2k; R_0603_1608Metric
R8, R9, R34, R38, R47, R51, R60, R64, R73, R77, R86, R90, R99, R103: 133k; R_0603_1608Metric
R10, R35, R48, R61, R74, R87, R100: 14.7k; R_0603_1608Metric
R11, R28, R41, R54, R67, R80, R93: 150; R_1206_3216Metric
U1, U2, U11, U12, U15, U16, U19, U20, U23, U24, U27, U28, U31, U32: RT9624CGQWA; DFN-8-1EP_2x2mm_P0.5mm_EP0.6x1.2mm_LeadsExtended
U3, U10, U14, U18, U22, U26, U30: LM311DR; SOIC-8_3.9x4.9mm_P1.27mm
U6, U13, U17, U21, U25, U29, U33: LM358; TSSOP-8_3x3mm_P0.65mm
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

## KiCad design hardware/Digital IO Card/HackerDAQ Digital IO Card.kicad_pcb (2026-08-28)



Board: 2 copper layers, 90.0 x 90.0 mm, 80 parts (16 on the bottom side), 84 nets.

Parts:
C1, C2, C3, C4, C5, C6, C7: 100nF; C_0603_1608Metric
D1, D2, D4: BAT54W; SOT-323_SC-70
D3: SMF5.0A; D_SMF
D5, D6, D7, D8, D9, D10, D11, D12, D13, D14, D15, D16, D17, D18, D19, D20: AA3528SURSK; AA3528
J1, J2, J3, J4: MiniFit_Jr_5569_08A2; Molex_Mini-Fit_Jr_5569-08A2_2x04_P4.20mm_Horizontal
J5: HEADER_3x1; PinHeader_1x03_P2.54mm_Vertical
J6: LD15S33E4GX00LF; Amphenol_LD15S33E4GX00LF
LG1: HackerDAQ Logo
R1, R2, R3, R4, R5, R7, R8, R9, R17, R18, R19, R20, R21, R22, R23, R24: 150; R_1206_3216Metric
R6, R10, R11, R12, R13, R14, R15, R16, R25, R26, R27, R28, R29, R30, R31, R32, R33, R34: 33; R_0603_1608Metric
R35: 10k; R_0603_1608Metric
U1, U2, U3, U4: SRV05-4.TCT; SOT-23-6
U5, U6, U7: SN74ACT17PWR; TSSOP-14_4.4x5mm_P0.65mm
U8: MCP23S17_SS; SSOP-28_5.3x10.2mm_P0.65mm
U9: M95320-RMN6; SOIC-8_3.9x4.9mm_P1.27mm
U10: SN74AHC1G125; SOT-23-5
U11: TXB0106PW; TSSOP-16_4.4x5mm_P0.65mm

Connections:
+3.3V: C7.1, J5.3, J6.5, R35.2, U10.5 (VCC), U11.2 (V_{CCA}), U11.8 (OE)
+5V: C1.1, C2.1, C3.1, J5.1, J6.3, U5.14 (V_{CC}), U6.14 (V_{CC}), U7.14 (V_{CC})
/IO0: J4.8, R30.1, U4.6 (IO4)
/IO0_LED: R7.2, U6.2 (1Y)
/IO1: J4.7, R29.2, U4.4 (IO3)
/IO1_LED: R22.2, U6.4 (2Y)
/IO2: J4.6, R15.1, U4.1 (IO1)
/IO2_LED: R8.2, U6.6 (3Y)
/IO3: J4.5, R12.2, U4.3 (IO2)
/IO3_LED: R23.2, U6.8 (4Y)
/IO4: J3.8, R28.1, U3.6 (IO4)
/IO4_LED: R9.2, U6.10 (5Y)
/IO5: J3.7, R27.2, U3.4 (IO3)
/IO5_LED: R24.2, U6.12 (6Y)
/IO6: J3.6, R14.1, U3.1 (IO1)
/IO6_LED: R17.2, U5.2 (1Y)
/IO7: J3.5, R11.2, U3.3 (IO2)
/IO7_LED: R1.2, U5.4 (2Y)
/IO8: J2.8, R26.1, U2.6 (IO4)
/IO8_LED: R18.2, U5.6 (3Y)
/IO9: J2.7, R25.2, U2.4 (IO3)
/IO9_LED: R2.2, U5.8 (4Y)
/IO10: J2.6, R13.1, U2.1 (IO1)
/IO10_LED: R3.2, U7.2 (1Y)
/IO11: J2.5, R10.2, U2.3 (IO2)
/IO11_LED: R19.2, U7.4 (2Y)
/IO12: J1.8, R32.1, U1.6 (IO4)
/IO12_LED: R4.2, U7.6 (3Y)
/IO13: J1.7, R31.2, U1.4 (IO3)
/IO13_LED: R20.2, U7.8 (4Y)
/IO14: J1.6, R16.1, U1.1 (IO1)
/IO14_LED: R5.2, U7.10 (5Y)
/IO15: J1.5, R6.2, U1.3 (IO2)
/IO15_LED: R21.2, U7.12 (6Y)
/IOExpander/PA0: R30.2, U7.13 (6A), U8.21 (GPA0)
/IOExpander/PA1: R29.1, U7.11 (5A), U8.22 (GPA1)
/IOExpander/PA2: R15.2, U7.9 (4A), U8.23 (GPA2)
/IOExpander/PA3: R12.1, U7.5 (3A), U8.24 (GPA3)
/IOExpander/PA4: R28.2, U7.3 (2A), U8.25 (GPA4)
/IOExpander/PA5: R27.1, U7.1 (1A), U8.26 (GPA5)
/IOExpander/PA6: R14.2, U5.9 (4A), U8.27 (GPA6)
/IOExpander/PA7: R11.1, U5.5 (3A), U8.28 (GPA7)
/IOExpander/PB0: R26.2, U5.3 (2A), U8.1 (GPB0)
/IOExpander/PB1: R25.1, U5.1 (1A), U8.2 (GPB1)
/IOExpander/PB2: R13.2, U6.13 (6A), U8.3 (GPB2)
/IOExpander/PB3: R10.1, U6.11 (5A), U8.4 (GPB3)
/IOExpander/PB4: R32.2, U6.9 (4A), U8.5 (GPB4)
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

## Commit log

2026-03-01 Initial commit, nearly done with voltage card
    [5V_To_3.3V_LDO.kicad_sch, AD7770_ADC.kicad_sch, B2B Connector Card Side.kicad_sch, HackerDAQ Voltage Card.kicad_pcb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]
2026-03-03 Finish initial voltage card design, add logo
    [HackerDAQ Voltage Card.kicad_pcb, HackerDAQ Voltage Card.kicad_sch, SPI_EEPROM.kicad_sch]
2026-03-08 Start on MCU symbol and main unit
    [5V_To_3.3V_LDO.kicad_sch, HackerDAQ Voltage Card.kicad_pcb, HackerDAQ Voltage Card.kicad_sch, MCU.kicad_sch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]
2026-03-08 Implement card connector schematic
    [5V_To_3.3V_LDO.kicad_sch, CardBusConnectors.kicad_sch, MCU.kicad_sch, Main Unit.kicad_pcb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]
2026-03-12 Add MicroSD card, finish MCU symbol
    [5V_To_3.3V_LDO.kicad_sch, CardBusConnectors.kicad_sch, MCU.kicad_sch, Main Unit.kicad_pcb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]
2026-03-14 Start on Digital IO card
    [DigitalIODriver.kicad_sch, HackerDAQ Digital IO Card.kicad_pcb, HackerDAQ Digital IO Card.kicad_sch, MCU.kicad_sch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]
2026-03-21 DIO card initial schematic done
    [DigitalIODriver.kicad_sch, HackerDAQ Digital IO Card.kicad_pcb, HackerDAQ Digital IO Card.kicad_sch, IOExpander.kicad_sch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]
2026-03-24 Start redoing DIO card
    [HackerDAQ Digital IO Card.kicad_pcb, HackerDAQ Digital IO Card.kicad_sch, IOExpander.kicad_sch, IOProtection.kicad_sch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]
2026-03-25 Finish redesigned DIO card
    [B2B Connector Card Side.kicad_sch, DigitalIODriver.kicad_sch, HackerDAQ Digital IO Card.kicad_pcb, HackerDAQ Digital IO Card.kicad_sch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]
2026-03-26 MCU schematic tweaks
    [MCU.kicad_sch]
2026-04-01 Implement Ethernet, start on voltage regulator
    [5V_To_3.3V_LDO.kicad_sch, DebugUSBUART.kicad_sch, EthernetInterface.kicad_sch, MCU.kicad_sch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]
2026-04-01 Finish 3.3V regulator
    [CardBusConnectors.kicad_sch, DebugUSBUART.kicad_sch, EthernetInterface.kicad_sch, MCU.kicad_sch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]
2026-04-28 Main unit: Add USB port for MCU and 3.3VA rail, start on routing
    [5V_To_3.3V_LDO.kicad_sch, CardBusConnectors.kicad_sch, DebugUSBUART.kicad_sch, EthernetInterface.kicad_sch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]
2026-05-01 Route most of the data lines on the PCB
    [EthernetInterface.kicad_sch, Main Unit.kicad_pcb, MicroSDCard.kicad_sch]
2026-05-03 Add schematic for Vsupply input
    [5V_To_3.3V_LDO.kicad_sch, MCU.kicad_sch, Main Unit.kicad_pcb, Main Unit.kicad_sch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]
2026-05-07 Route more of main unit, start on KiBot CI job
    [5V_To_3.3V_LDO.kicad_sch, AD7770_ADC.kicad_sch, B2B Connector Card Side.kicad_sch, HackerDAQ Voltage Card.kicad_pcb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]
2026-05-07 Add Main Unit to CI build as well
    [5V_To_3.3V_LDO.kicad_sch, AD7770_ADC.kicad_sch, HackerDAQ Main Unit.kicad_pcb, HackerDAQ Main Unit.kicad_sch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]
2026-05-07 Add Voltage Card Rev 1rc1 export
    [HackerDAQ Main Unit.kicad_pcb, HackerDAQ Voltage Card-NPTH.drl, HackerDAQ Voltage Card-bom-pcbinv.csv, HackerDAQ Voltage Card.brd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]
2026-05-09 Add LEDs and 5V regulator to main unit
    [5V_To_3.3V_LDO.kicad_sch, CardBusConnectors.kicad_sch, DebugUSBUART.kicad_sch, EthernetInterface.kicad_sch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]
2026-05-10 Main board routed!!
    [EthernetInterface.kicad_sch, HackerDAQ Main Unit.kicad_pcb, HackerDAQ Main Unit.kicad_sch, MCU.kicad_sch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]
2026-05-10 Geographical reannotate
    [5V_To_3.3V_LDO.kicad_sch, CardBusConnectors.kicad_sch, DebugUSBUART.kicad_sch, EthernetInterface.kicad_sch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]
2026-05-10 Try to fix USB port model path
    [HackerDAQ Main Unit.kicad_pcb]
2026-05-10 DRC weirdness
    [HackerDAQ Main Unit.kicad_pcb]
2026-05-10 OK looks like .wrl files are not supported anymore by KiBot
    [HackerDAQ Main Unit.kicad_pcb]
2026-05-10 Release of main unit rc1!
    [HackerDAQ Main Unit-NPTH.drl, HackerDAQ Main Unit-bom-pcbinv.csv, HackerDAQ Main Unit.brd, HackerDAQ Main Unit.drl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]
2026-05-11 Update solder mask settings to fix PCBWay DFM issue
    [HackerDAQ Main Unit.gbl, HackerDAQ Main Unit.gbo, HackerDAQ Main Unit.gbp, HackerDAQ Main Unit.gbs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]
